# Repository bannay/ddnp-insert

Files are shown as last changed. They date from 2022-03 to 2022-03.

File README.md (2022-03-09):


<!-- PROJECT LOGO -->
<br />
<div align="center">
  <a href="https://github.com/bannay/ddnp-insert">
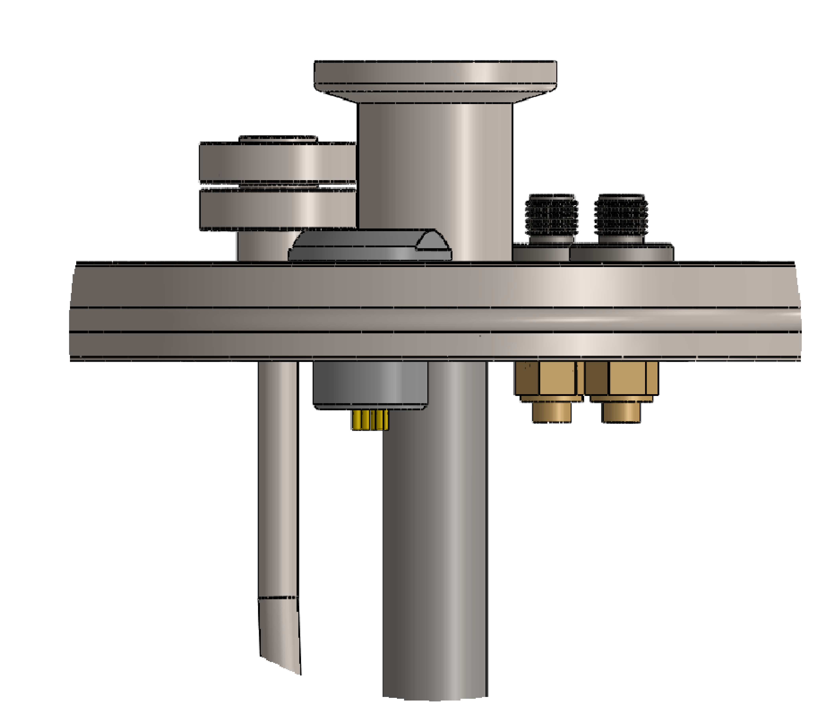
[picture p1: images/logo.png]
    
  </a>
<br>

<h3 align="center">A single sample dissolution DNP insert</h3>
</div>

<!-- ABOUT THE PROJECT -->
## **About the project**
The dDNP insert is responsible for centering the sample in the homogeneous region of the magnet and provide sample access to microwave irradiation, RF circuitry and dissolution. The insert is designed to minimize manufacturing complexity, cost and static heat loads when in the magnet’s cryostat. More detials can be found in the following article:

[Albannay, M. M., Vinther, J. M. O., Petersen, J. R., Zhurbenko, V. & Ardenkjaer-Larsen, J. H. Compact, low-cost NMR spectrometer and probe for dissolution DNP. J. Magn. Reson. 304, 7–15 (2019)](https://www.sciencedirect.com/science/article/abs/pii/S1090780719300825)

### Designed with
* Solidworks 2019
***

<!-- TABLE OF CONTENTS -->
<details open="open">
  <summary><h2 style="display: inline-block">Table of Contents</h2></summary>
  <ol>
    <li>
      <a href="#about">About</a>
    </li>
    <li>
    <a href="#design-and-construction">Design and construction</a>
    <ul>
        <li><a href="#cryostat-flange">Cryostat flange</a></li>
        <li><a href="#top-flange">Top flange</a></li>
        <li><a href="#sample-port">Sample port</a></li>
        <li><a href="#sample-tube">Sample tube</a></li>
        <li><a href="#purging-chamber">Purging Chamber</a></li>
        <li><a href="#baffles">Baffles</a></li>
        <li><a href="#waveguide">Waveguide</a></li>
        <li><a href="#modified-ug387-flange-and-mate">Modified UG387 flange and mate</a></li>
        <li><a href="#microwave-cavity">Microwave cavity</a></li>
    </ul>
    </li>
  </ol>
</details>

***

## Design and construction

<p align="center">
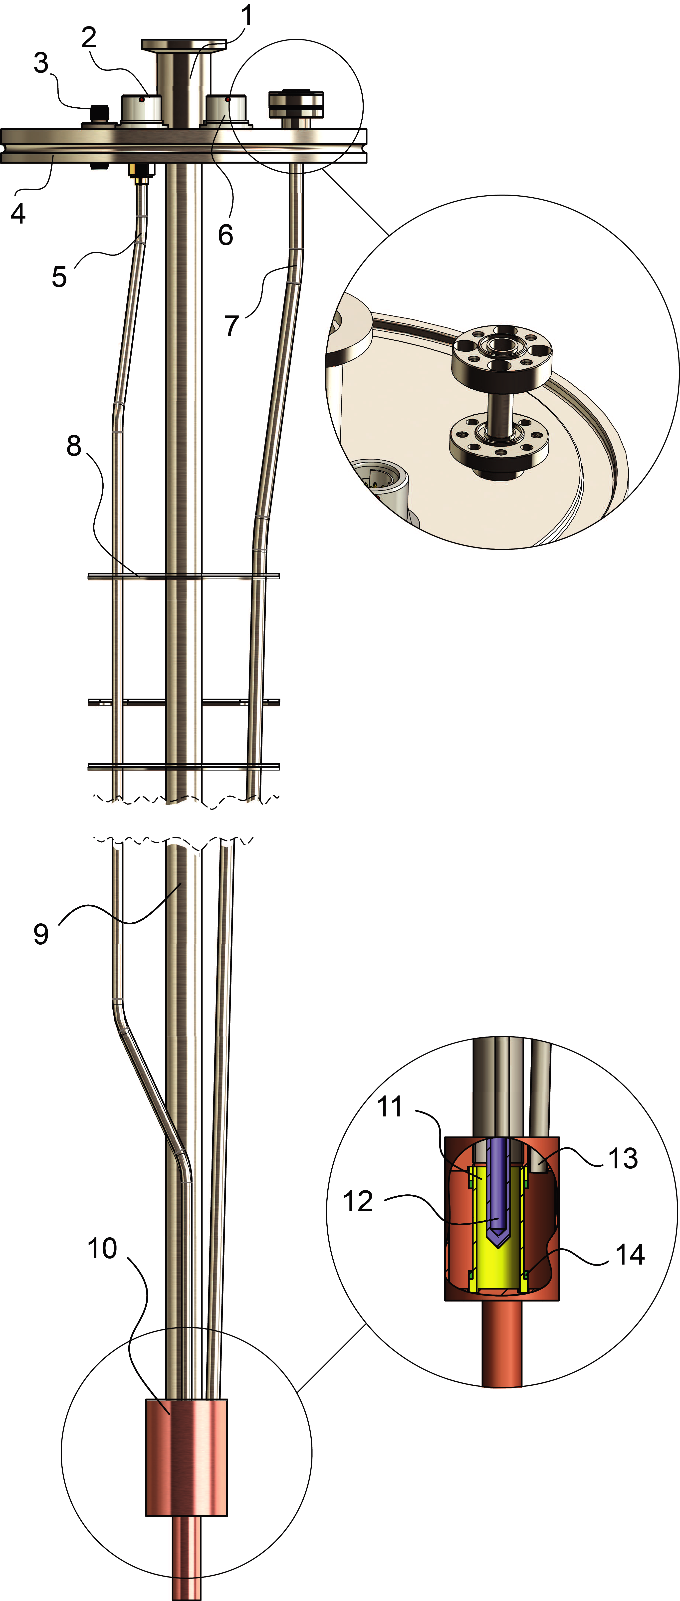
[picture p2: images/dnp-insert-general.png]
dnp-insert-general
  
</p>

*dDNP insert illustration. 1.sample loading port, 2. & 6. thermometry and helium level sensing connector, 3. hepatic SMA connector, 4. ISO-63 flange, 5. UT141SS-C-P coaxial cable, 7. waveguide, 8. baffles, 9. sample tube, 10. overmoded cavity, 11. PTFE coil former, 12. sample vial, 13. waveguide outlet, 14. Sample coil (green). Not illustrated: second hepatic SMA connector (positioned behind component 2.). Inset illustrates modified UG387 waveguide flange and coupling flange*

<p align="right">(<a href="#top">back to top</a>)</p>

***

### Cryostat flange

The insert fits in an Oxford Instruments STD Spectrostat 86/62 cryostat. A cryostat flange receives the insert facilitates a pumping outlet (KF-40). The bottom plate presses on an O-ring atop the cryostat and is screwed with 4 M5 screws. The cryostat flange is a two piece assembly constructed from 304L stainless steel and is vacuum welded together.

<p align="center">
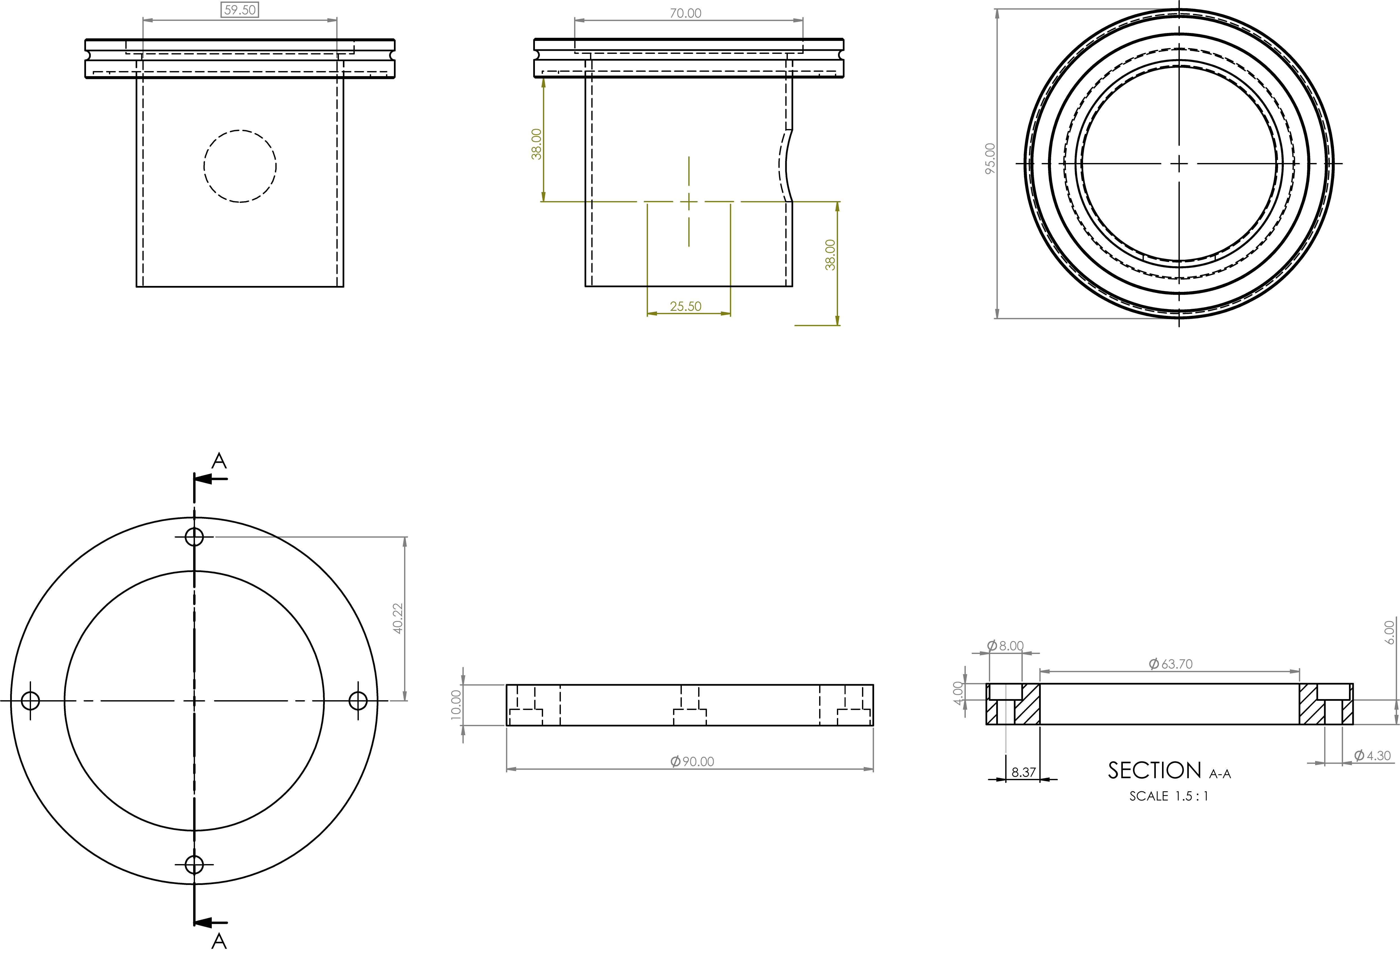
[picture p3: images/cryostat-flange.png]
cryostat-flange
  
</p>

<p align="right">(<a href="#top">back to top</a>)</p>

***

### Top flange
304L stainless-steel ISO-63 flange, mates with the top of the cryostat using a centering ring equipped with an O-ring and three/four claw clamps. The flange houses multiple connectors; two hermetic bulkhead female-to-female SMA connectors (SF2991-6002,SV microwaves, FL, USA) to access the RF circuitry and two hermetic low voltage connectors (Fischer, St-Prex, Switzerland OR LEMO, Écublens, Switzerland) for helium level sensing and thermometry. Varnished 32 AWG Phosphor bronze wires are used to connect the two low voltage connectors with the sensors placed on the insert cavity. The wire thickness and material offer low thermal conductivity and high electrical resistivity. Brazed on the ISO-63 is a modified UG387 flange with four additional threaded M2 holes and an O-ring to receive a waveguide at a later stage. O-rings are lightly coated with cryogenic grease (Apiezon N, M & I Materials Ltd, Manchester, UK) to improve their seal under vacuum.

<p align="center">
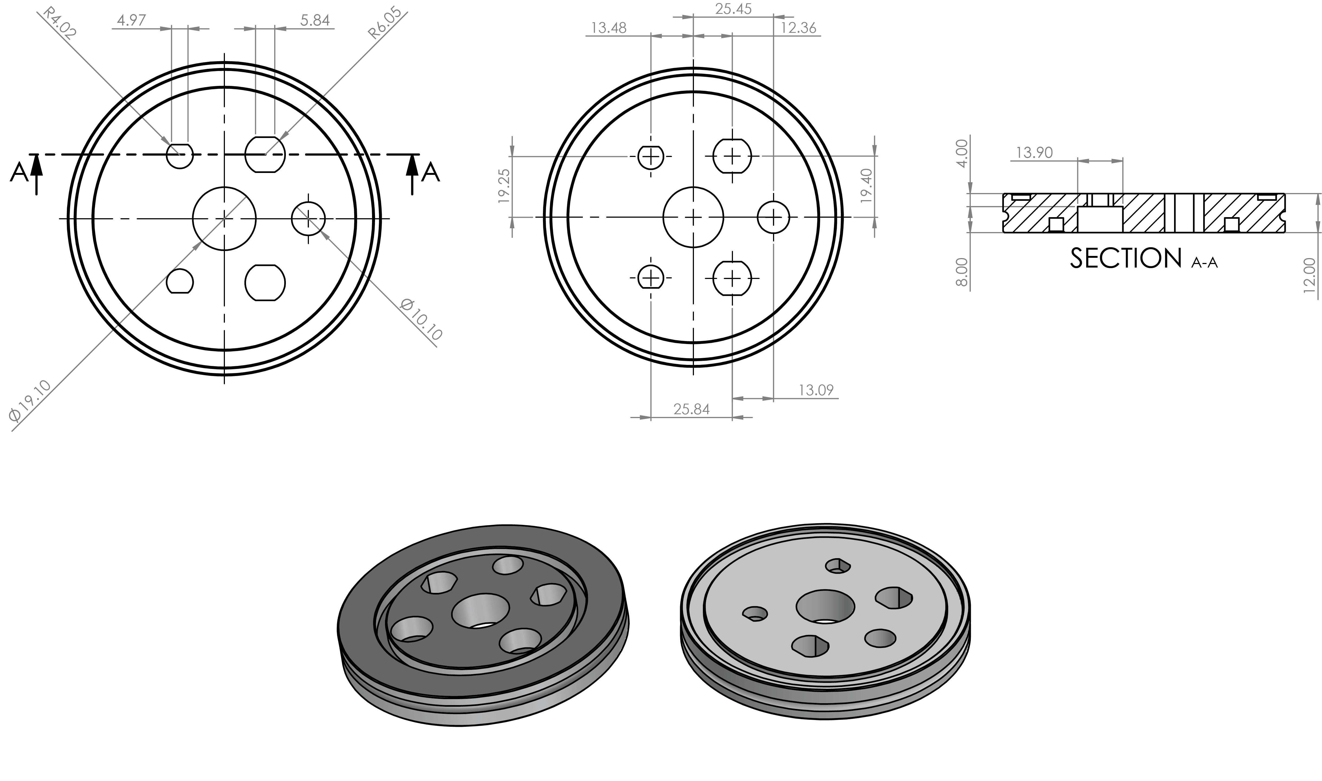
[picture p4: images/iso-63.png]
top-flange
  
</p>

<p align="right">(<a href="#top">back to top</a>)</p>

***

### Sample port

The sample port was machined as whole from 304L stainless steel, slotted into the top flange (ISO-63) and vacuum-tight welded from top and below. A gate valve (01224-KA24VAT, VAT, Switzerland) and airlock adapted install above the KF16 flange.

<p align="center">
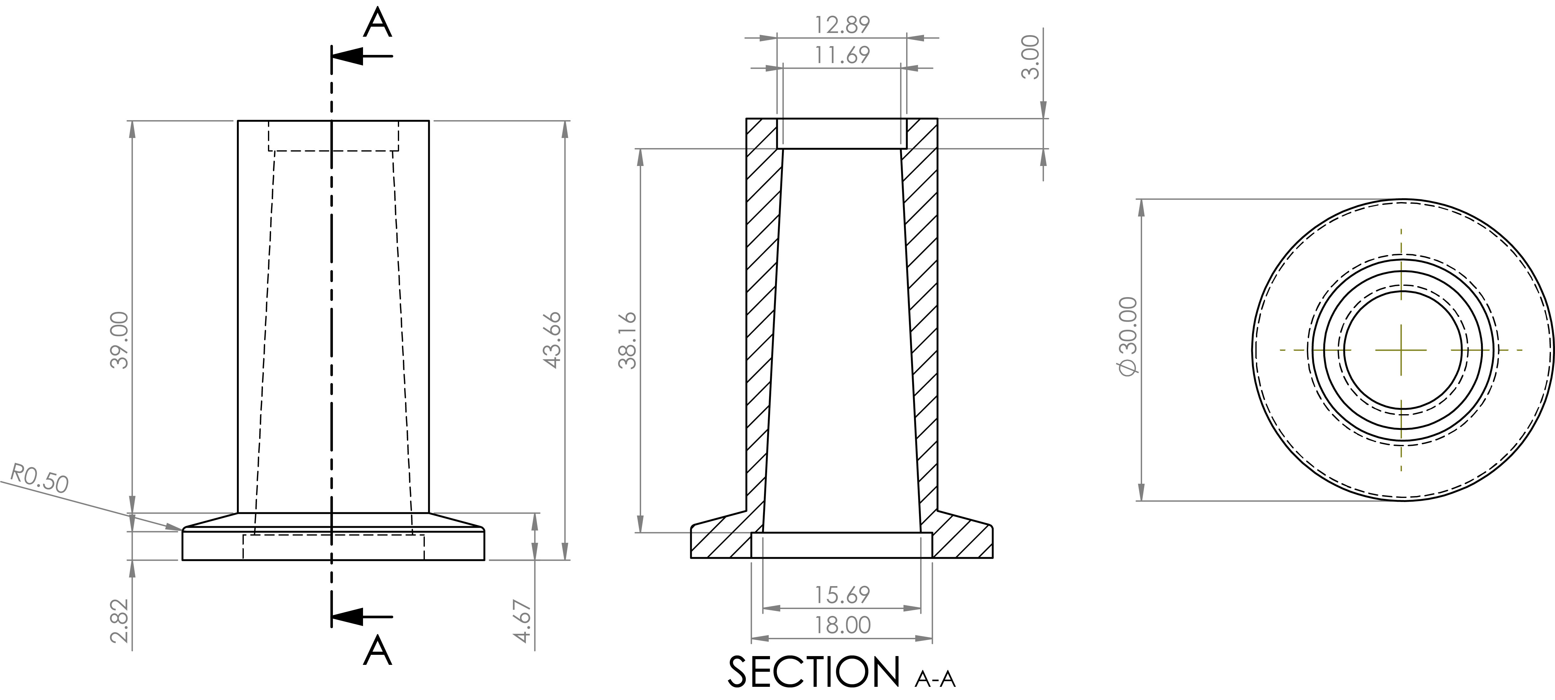
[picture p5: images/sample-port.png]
sample-port
  
</p>

<p align="right">(<a href="#top">back to top</a>)</p>

***

### Sample tube

Sample tube: 304L stainless-steel tube (Wellington Tube Supplies Ltd, Hayes, UK)
(ID = 11.8±0.2 mm, OD = 12.7±0.2mm and h = 790±1 mm) is slotted through the top flange and into the sample port. A weld joint between the sample port and the sample tube wall secures the assembly. 

<p align="right">(<a href="#top">back to top</a>)</p>

***

### Purging chamber

The purging chamber receives a sample tethered via a fluid path/PEEK tube with a dynamic O-ring seal from the top and mates to a gate valve at the bottom (KF-16 flange). Prior to introducing the sample into the cryostat the atmosphere surrounding the vial is to be flushed with helium to mitigate blockage in the cryostat capillary. Not illustrate is the purging inlet, which is simply a threaded hole that matches the appropriate Legris/SMC gas quick connector.

<p align="center">
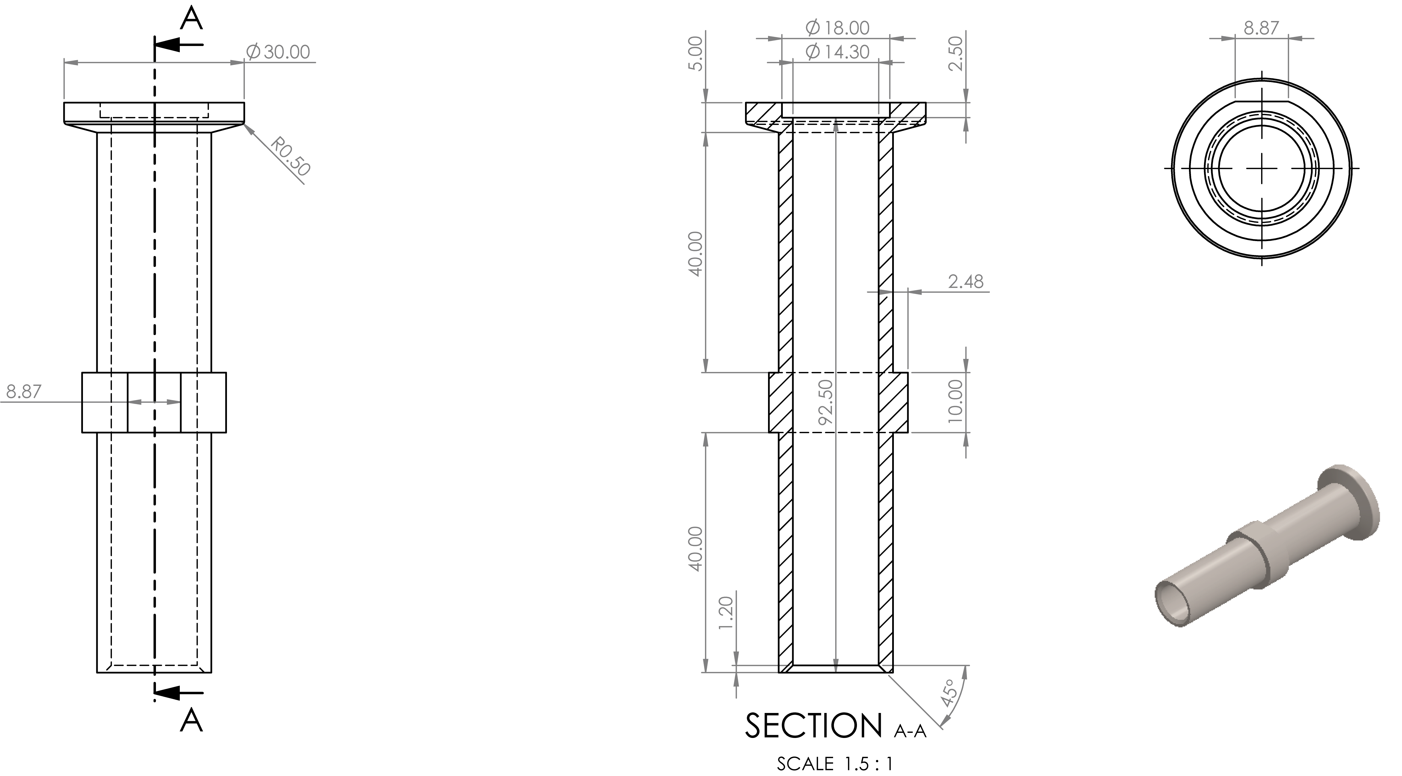
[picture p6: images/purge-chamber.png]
purge-chamber
  
</p>

<p align="right">(<a href="#top">back to top</a>)</p>

***

### Baffles 

316L stainless steel sheets are cut to produce 4 semi-circle baffles (r =
57 mm and t = 1±0.2 mm) and welded to the sample tube. The baffles mitigate black-body radiation a towards the sample from the room temperature top flange and improve thermoacoustic stability. There are 3 semi-circle cuts in the baffles to accommodate the sample tube, waveguide and coaxial cable(s). The middle two baffles are spaced 22 mm apart, while 110 mm separate the top and bottom baffles. The top baffle is positioned 145 mm from the top flange

<p align="center">
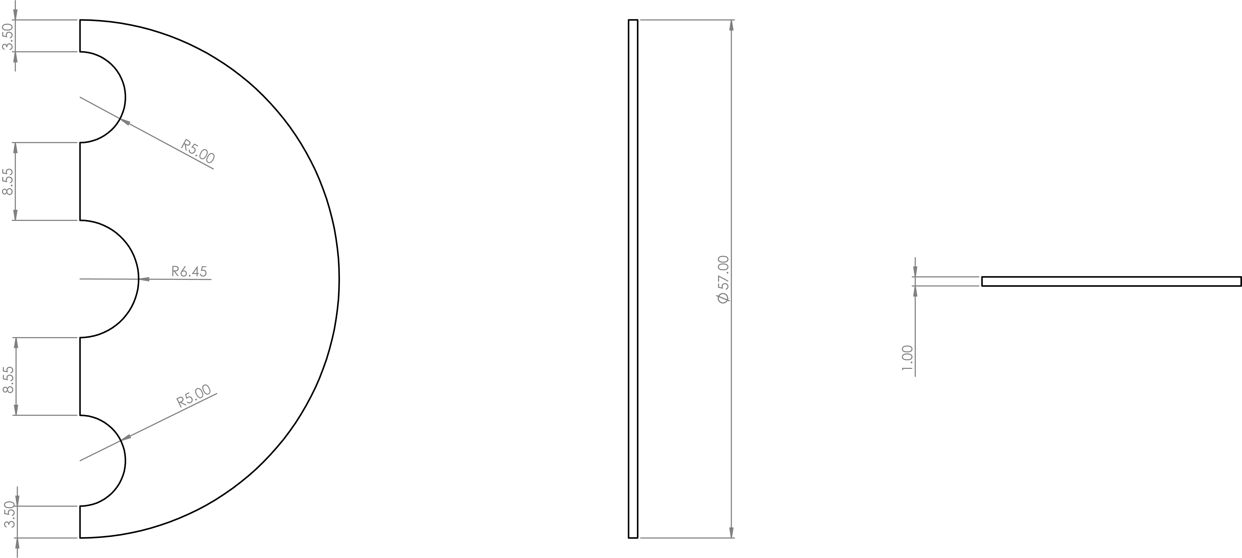
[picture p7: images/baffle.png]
baffle
  
</p>

<p align="right">(<a href="#top">back to top</a>)</p>

***

### Waveguide 

316L seamless stainless-steel tube (Wellington Tube Supplies Ltd, Hayes,
UK) (ID = 4.16±0.2 mm, OD = 4.80±0.2 mm and h = 780±1 mm) is welded to a modified UG387 flange hosting an O-ring.

<p align="right">(<a href="#top">back to top</a>)</p>

***

### Modified UG387 flange and mate

The purpose of the modified UG387 flange is to allow coupling between the waveguide and microwave source. The UG387 mate found on the ISO-63 flange is to designed to accommodate the waveguide into the insert while ensuring vacuum tight mechanical coupling. Both parts are machined from 304 L stainless steel.

<p align="center">
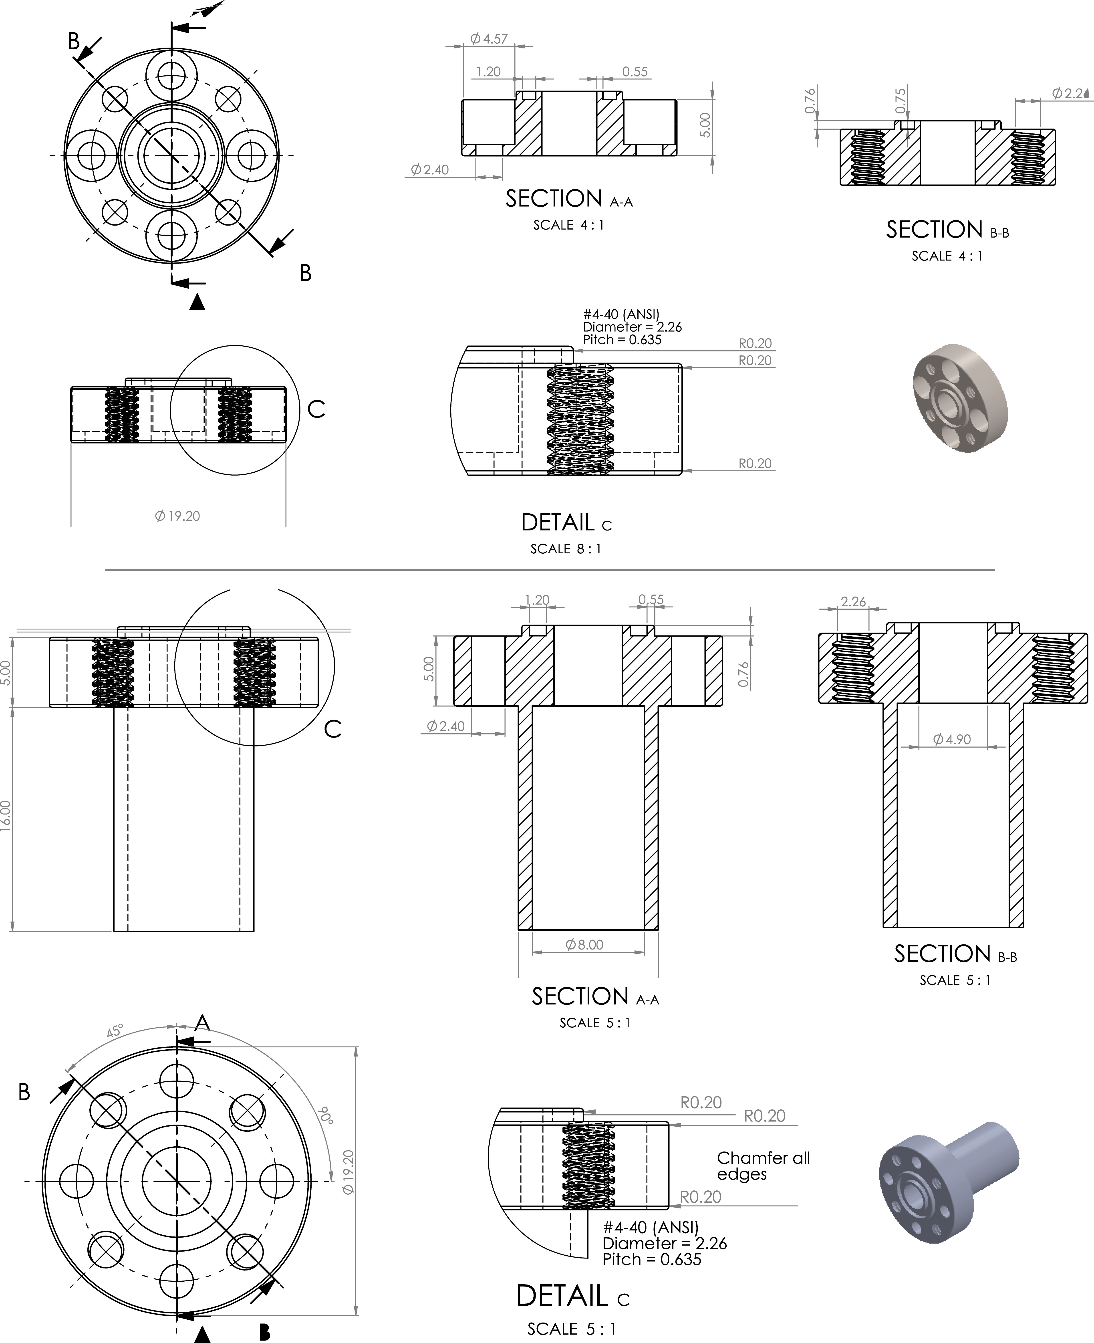
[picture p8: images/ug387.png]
  
</p>

<p align="right">(<a href="#top">back to top</a>)</p>

***

### Microwave cavity
The cavity is a three-part assembly. The first part is a copper ring constituting
the cavity upper (ID = 27.5±0.2 mm, OD = 12.9±0.2 mm and h = 7±0.2 mm) is welded onto the sample tube. Second, the lower cavity is made from a cylindrical copper can (ID = 28.0±0.2 mm, and h = 30.0±0.2 mm) that tightly fits around the cavity upper and secures to it by two brass M1 screws. Two circular grooves milled in the cavity upper and lower (ID = 13.0±0.2 mm, OD = 15.0±0.2 mm and h = 1.0±0.2 mm) accommodate the coil and coil former. The third part is the cavity tail which is a copper cylinder (OD = 15.0±0.2 mm and h = 20-35 mm) with a threaded hole. The tail is screwed to the cavity lower using a brass M3 screw.

<p align="center">
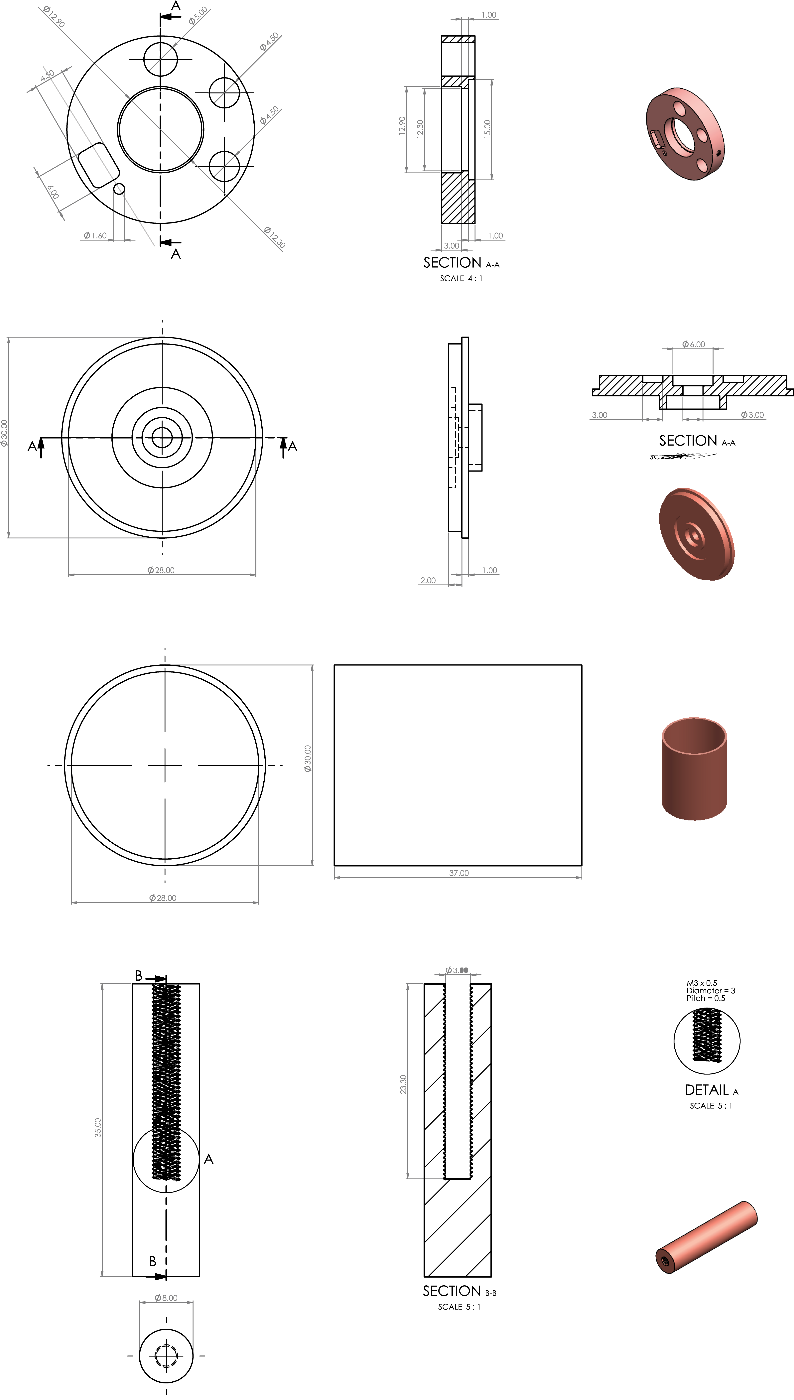
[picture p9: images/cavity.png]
cavity
  
</p>

<p align="right">(<a href="#top">back to top</a>)</p>

***

<!-- LICENSE -->
## License

Distributed under the MIT License. See `LICENSE.txt` for more information.

<!-- CONTACT -->
## Contact

Mohammed M. Albannay - [@Bannay](https://twitter.com/bannay) - bannay@gmail.com

Project Link: [https://github.com/bannay/ddnp-insert](https://github.com/bannay/ddnp-insert)

***

<!-- ACKNOWLEDGMENTS -->
## Acknowledgments

* [Readme template](https://github.com/othneildrew/Best-README-Template)

<p align="right">(<a href="#top">back to top</a>)</p>

***

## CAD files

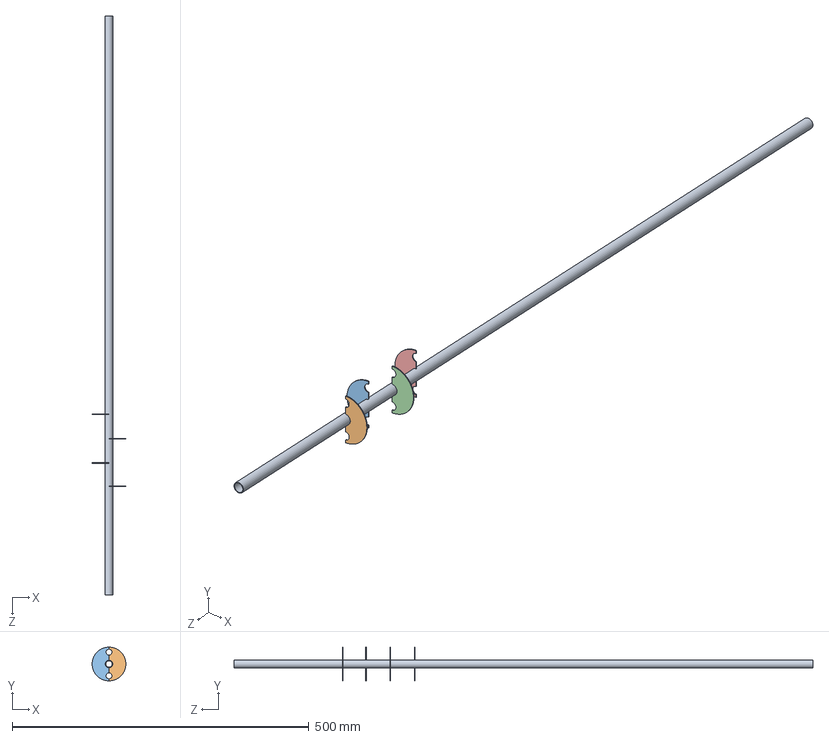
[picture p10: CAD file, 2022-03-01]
CAD/Assemblies/LPC_SampleTube.SLDASM
57.0 x 57.0 x 976.0 mm
SampleTube_1615
Baffle1
Baffle2
Baffle3
Baffle4

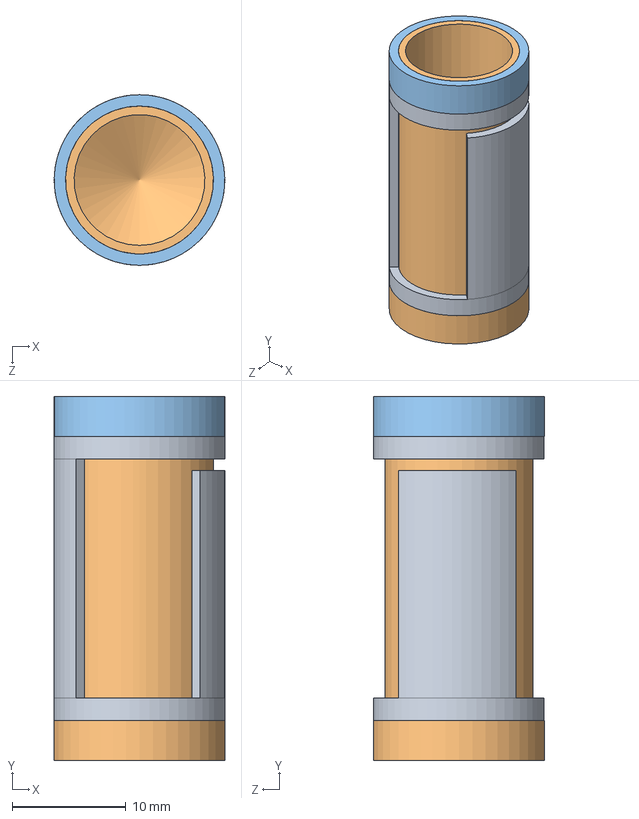
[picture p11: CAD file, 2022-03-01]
CAD/Insert/NMR coil/AldermanGrantASSY.SLDASM
15.0 x 32.0 x 15.0 mm
AldermanGrantCoil
CoilFormer
CoilFormerTop

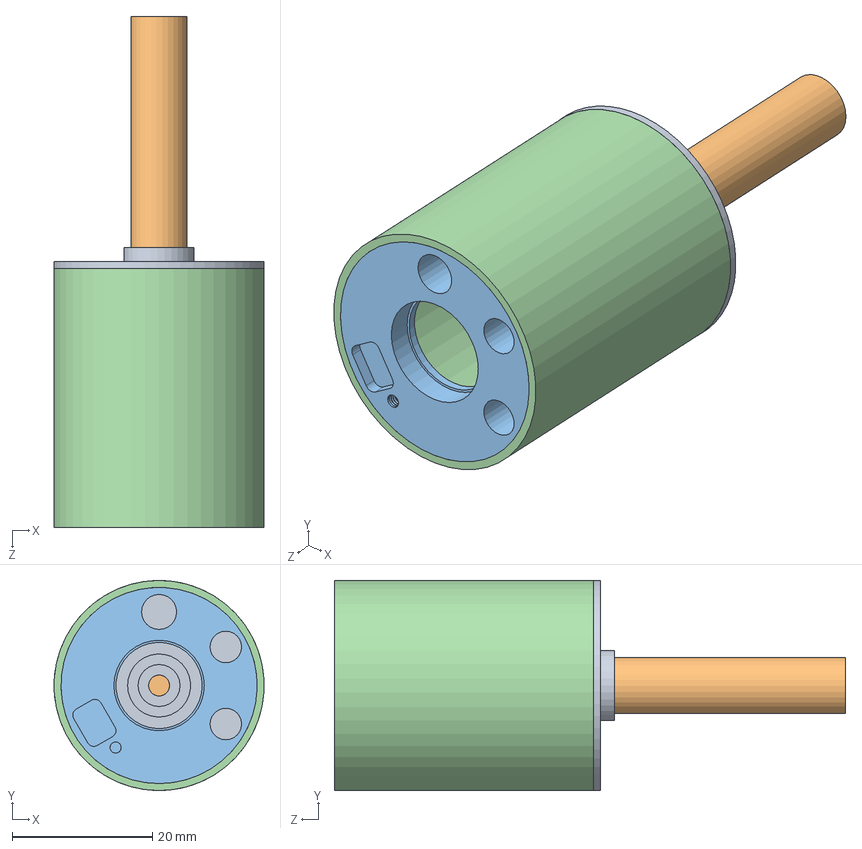
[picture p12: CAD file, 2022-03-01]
CAD/Assemblies/LPC_Cavity.SLDASM
30.0 x 30.0 x 73.0 mm
CavityLower_20039-20
CavityTail_20039-4
CavityUpper_20039-20
ChamberWalls_20061-13

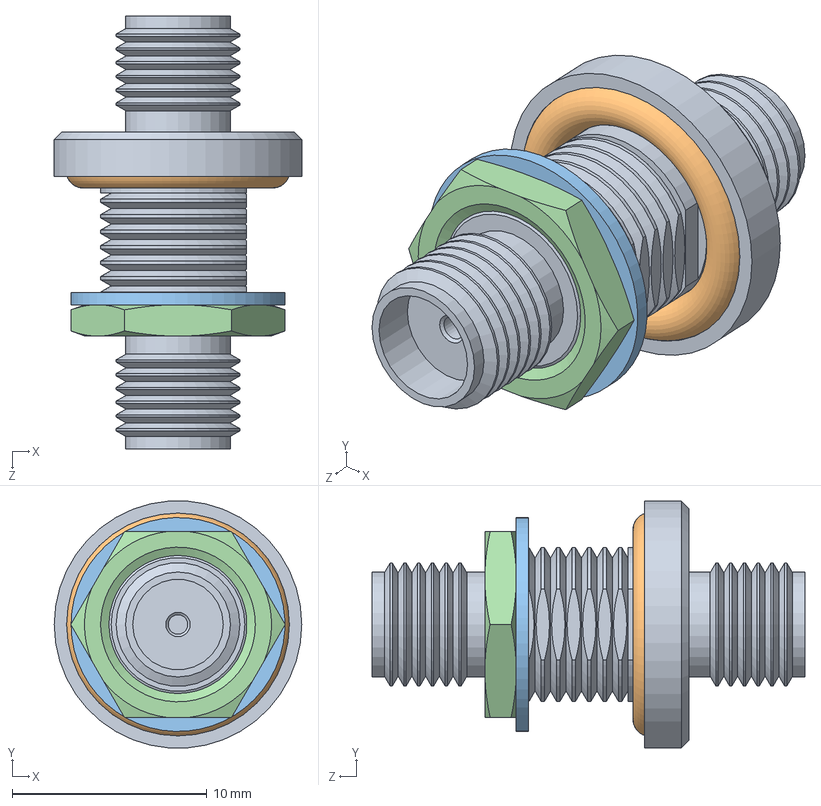
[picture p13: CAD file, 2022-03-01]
CAD/Insert/RF SMA SF2991-6002/SMA Female to Female Bulkhead Hermetic Adapter ASSY.SLDASM
12.7 x 12.7 x 22.2 mm
SMA Female to Female Bulkhead Hermetic Adapter Body
SMA Female to Female Bulkhead Hermetic Adapter O-ring
SMA Female to Female Bulkhead Hermetic Adapter Washer
SMA Female to Female Bulkhead Hermetic Adapter Nut

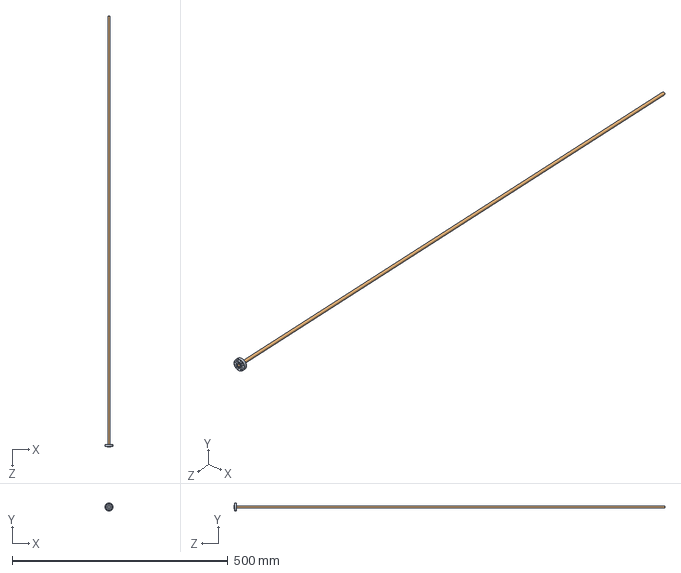
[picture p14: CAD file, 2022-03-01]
CAD/Insert/Waveguide/WaveguideAssembly.SLDASM
19.2 x 19.2 x 1000.0 mm
UG387_1_O-ring-blind
Waveguide

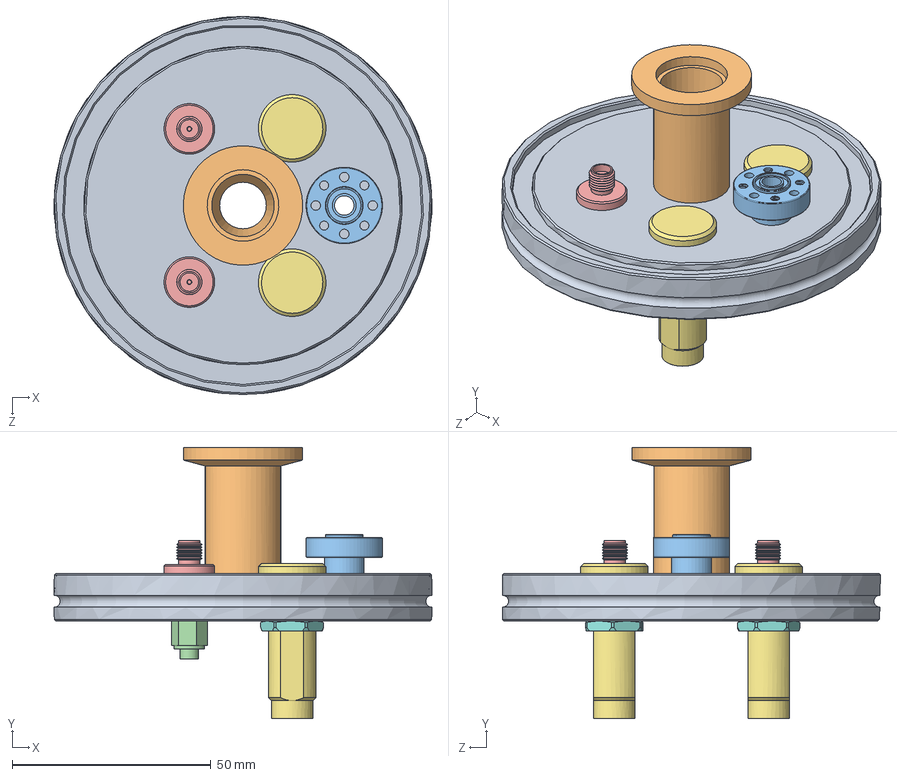
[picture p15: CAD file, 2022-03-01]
CAD/Assemblies/LPC_TopFlange.SLDASM
94.9 x 68.2 x 95.0 mm
TopFlange_ISO63B
SamplePort_KF16-machined
UG387_WaveguideHolder
SMA coax connector x 2
SMA Female to Female Bulkhead Hermetic Adapter Body x 2
SMA Female to Female Bulkhead Hermetic Adapter Nut x 2
LEMO_Body_SWH.1S.306.CLLPV x 2
LEMO_Nut_SWH.1S.306.CLLPV x 2

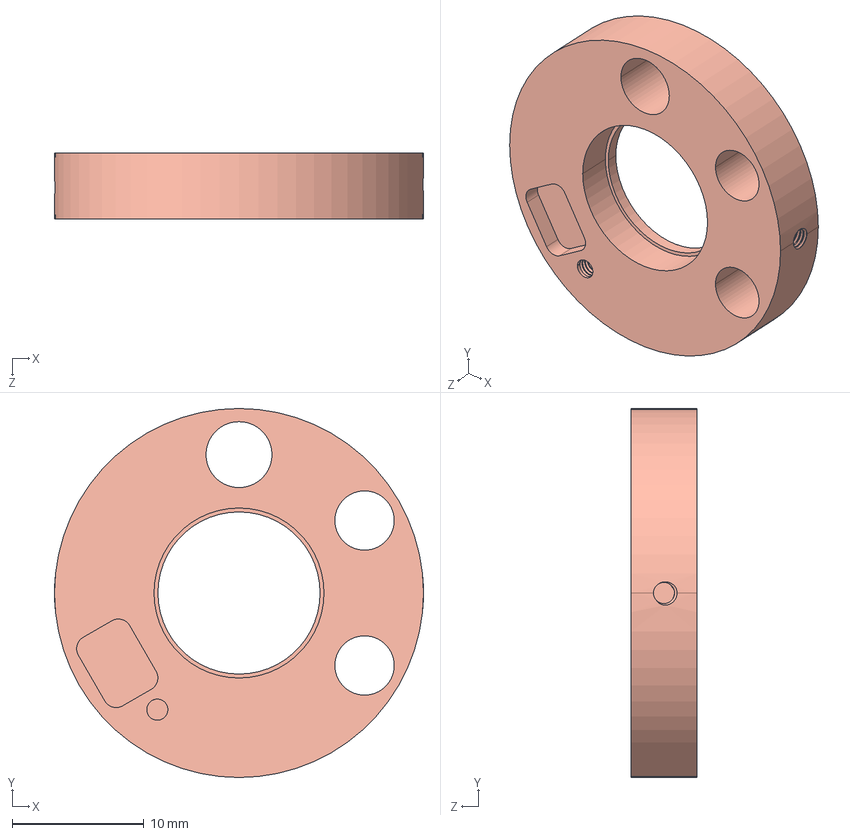
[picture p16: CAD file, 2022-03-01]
CAD/Cavity/CavityUpper_20039-20.STEP
28.0 x 28.0 x 5.00 mm

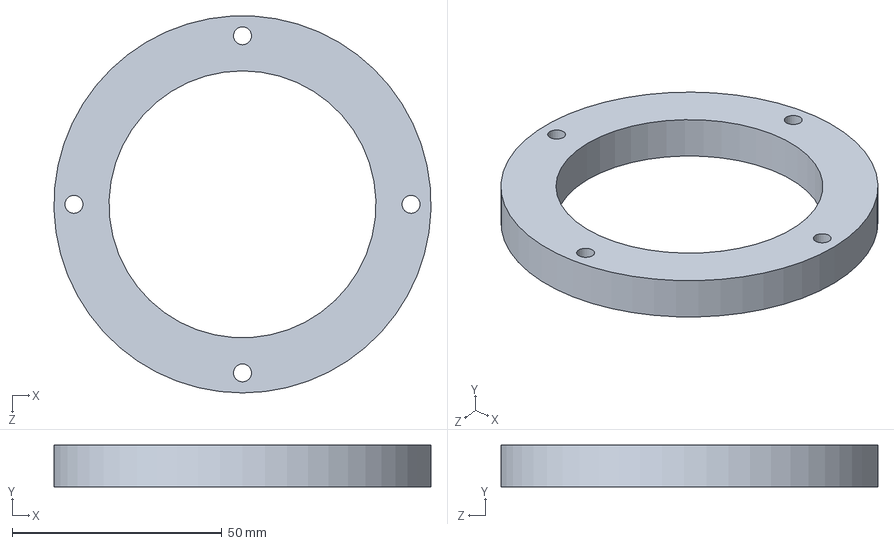
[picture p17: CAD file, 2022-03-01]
CAD/Cryostat flange/LowerFlange.SLDPRT
90.0 x 10.0 x 89.9 mm

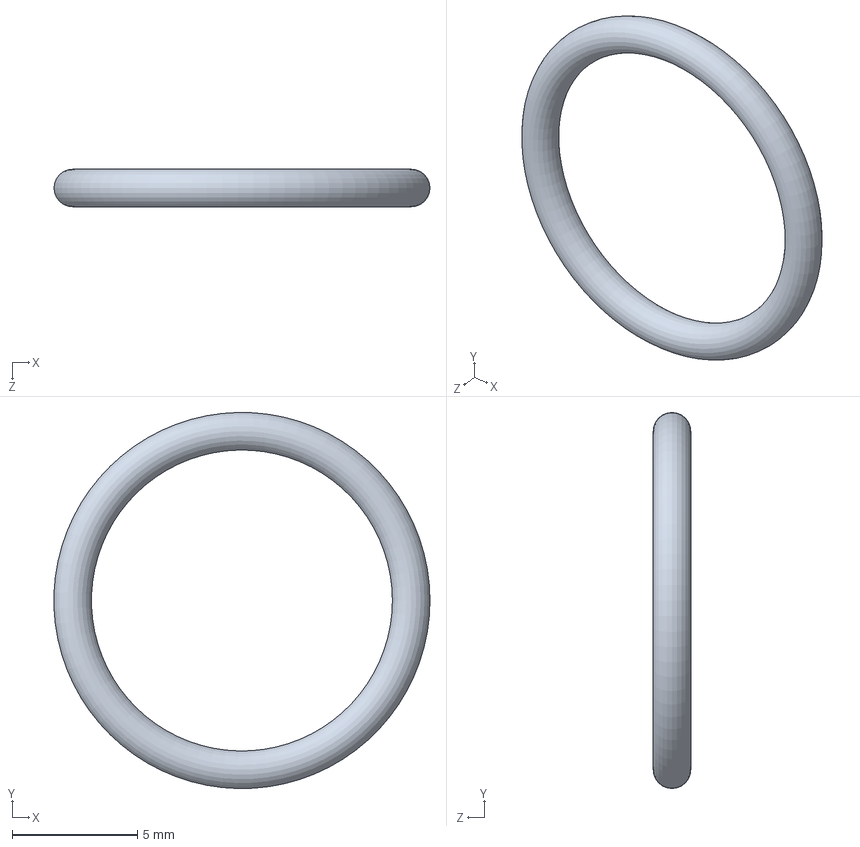
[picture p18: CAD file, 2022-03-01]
CAD/Insert/LEMO SWH.1S.306.CLLPV/LEMO_Oring_SWH.1S.306.CLLPV.SLDPRT
15.0 x 15.0 x 1.50 mm

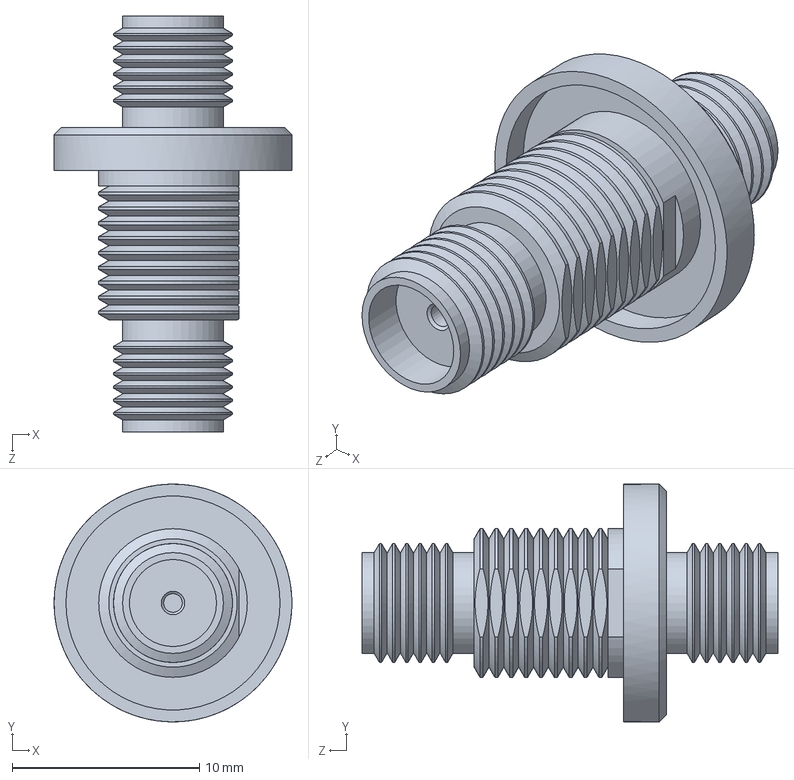
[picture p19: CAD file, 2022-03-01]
CAD/Insert/RF SMA SF2991-6002/SMA Female to Female Bulkhead Hermetic Adapter Body.SLDPRT
12.7 x 12.7 x 22.2 mm

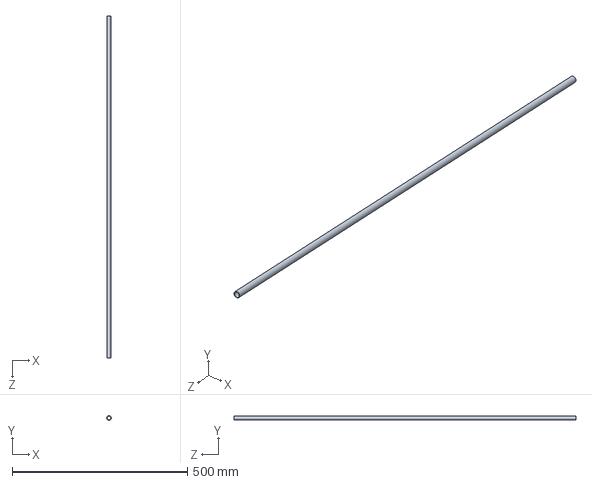
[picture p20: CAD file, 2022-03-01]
CAD/Insert/SampleTube_1615.SLDPRT
12.7 x 12.7 x 976.0 mm

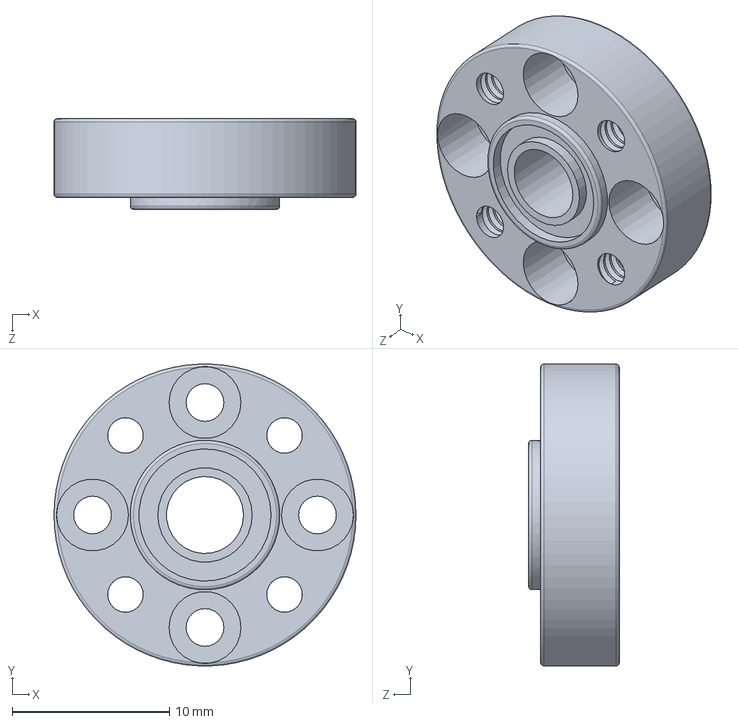
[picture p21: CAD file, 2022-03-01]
CAD/Insert/Waveguide/UG387_1_O-ring-blind.SLDPRT
19.2 x 19.2 x 5.76 mm

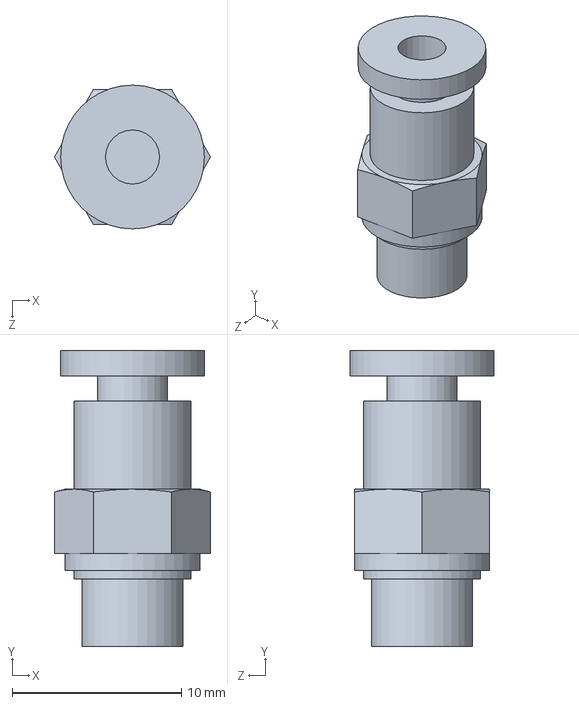
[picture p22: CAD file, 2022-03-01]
CAD/Loading purge chamber/KAH23-M6.SLDPRT
9.24 x 17.5 x 8.50 mm

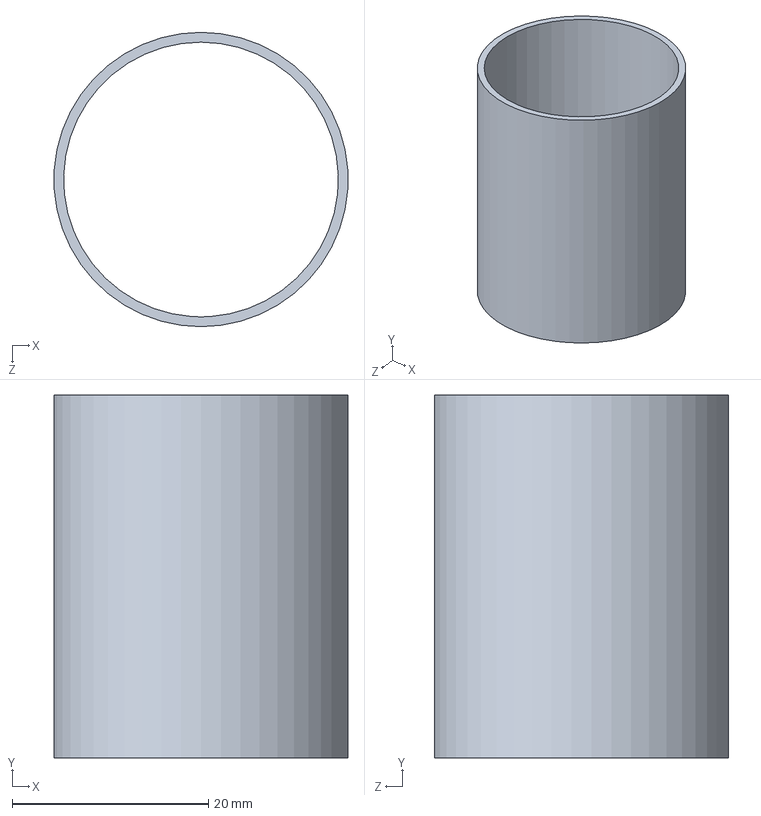
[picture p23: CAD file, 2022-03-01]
CAD/Cavity/ChamberWalls_20061-13.SLDPRT
29.9 x 37.0 x 30.0 mm

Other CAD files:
CAD/Loading purge chamber/CenteringRing_KF16.SLDASM
CAD/Cavity/Cavity.SLDASM
CAD/Cryostat flange/CenteringRing _ISO63AV.SLDPRT
CAD/Insert/Baffle1.SLDPRT
CAD/Cavity/CavityLower_20039-20.SLDPRT
CAD/Cavity/CavityTail_20039-4.SLDPRT
CAD/Cavity/CavityUpper_20039-20.SLDPRT
CAD/Cryostat flange/CryostatFlange.SLDASM
CAD/Cryostat flange/CryostatFlange.STEP
CAD/Cryostat flange/Hositrad_ISO63-64NH.SLDPRT
CAD/Cryostat flange/Hositrad_KF25-25-70.SLDPRT
CAD/Insert/Baffle2.SLDPRT
CAD/Insert/Baffle3.SLDPRT
CAD/Insert/Baffle4.SLDPRT
CAD/Insert/LEMO SWH.1S.306.CLLPV/LEMO_Body_SWH.1S.306.CLLPV.SLDPRT
CAD/Insert/LEMO SWH.1S.306.CLLPV/LEMO_Nut_SWH.1S.306.CLLPV.SLDPRT
CAD/Insert/NMR coil/AldermanGrantCoil.SLDPRT
CAD/Insert/NMR coil/CoilFormer.SLDPRT
CAD/Insert/NMR coil/CoilFormerTop.SLDPRT
CAD/Insert/RF SMA SF2991-6002/SMA Female to Female Bulkhead Hermetic Adapter Nut.SLDPRT
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
